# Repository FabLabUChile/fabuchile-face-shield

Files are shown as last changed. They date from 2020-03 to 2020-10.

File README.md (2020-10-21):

# Fablab U Chile Face Shield
Spanish version [here](/LEEME.md) | Versión en español [acá](/LEEME.md)

## Table of contents

- [Resume](#resume)
  * [Security and effectiveness validation](#security-and-effectiveness-validation)
- [Versions](#versions)
    + [LAST VERSION -> v6](#last-version----v6)
    + [v5 (can be stacked)](#v5--can-be-stacked-)
    + [v4](#v4)
    + [v3](#v3)
    + [v2](#v2)
    + [v1](#v1)
- [Parts](#parts)
  * [3D Printed Headband](#3d-printed-headband)
    + [Printer Settings](#printer-settings)
  * [Commercial Parts](#commercial-parts)
    + [Clear plastic sheet](#clear-plastic-sheet)
    + [Rubber band](#rubber-band)
- [Assembly](#assembly)
- [Sterilization and safety recommendations](#sterilization-and-safety-recommendations)
- [Join the community](#join-the-community)
- [License](#license)

<small><i><a href='http://ecotrust-canada.github.io/markdown-toc/'>Table of contents generated with markdown-toc</a></i></small>

## Resume

Based on the [Prusa Face Shield](https://www.prusaprinters.org/prints/25857-protective-face-shield-rc3) initiative, we design our own face shield in order to eliminate any further work on the comercial parts, and to match with the local availability of them,  decreasing the chance of contamination during the fabrication stage and for direct assembly. The face shield is meant to be used complementary with a N95 mask or similiar.

**Warning**: only V6.0 is a certificate medical device.

### Security and effectiveness validation

Recently, we subjected the V6.0 of the FaceShield to laboratory tests ([LICTEX USACH](https://www.linkedin.com/company/lictex-udesantiago/?originalSubdomain=cl)) to validate the performance of the Facial Shield (*)(**). The tests carried out were:
 1. Protection of standard point protected areas
 2. Protection against drops and liquid splashes
 3. Evaluation of lateral protection
 4. Evaluation of the Visual Field.

 (*) These tests are verified by the Chilean Institute of Public Health ([ISP](http://www.ispch.cl/)).
The Face Shield successfully passed all tests.

  (**) According to the standard of Facial Shields market in Chile, a fifth test is required, that of fogging. As we know, in Chile there are no laboratories that can carry out this test.

## Versions

#### LAST VERSION -> v6

The new version has several modifications in order to ensure protection over other factors:
* We increased the distances between the side flaps to use a legal size (~330 mm) translucent sheet. This modification gives more protection to the sides of the face.
* We added a cover in top of the shield to protect the face from particles that may attack from above.
* The cover increase the stiffness of the faceshield so we give more comfort by separating the side bars from the front part, also making it compliant for different head's sizes.

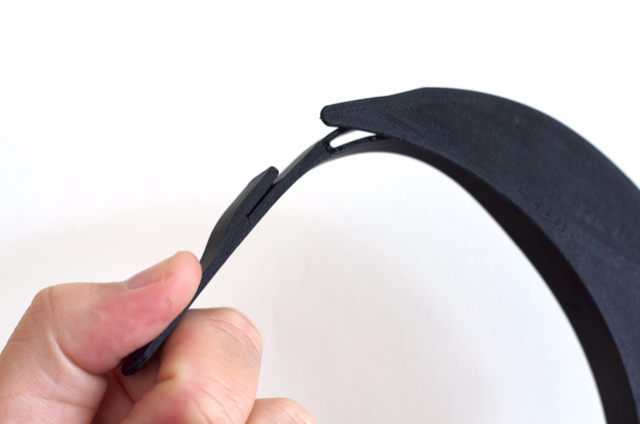
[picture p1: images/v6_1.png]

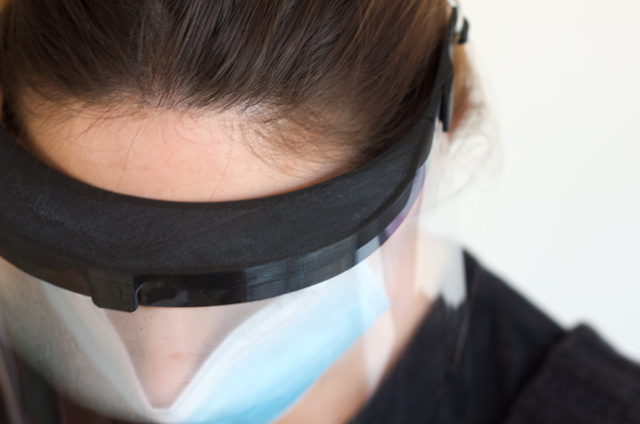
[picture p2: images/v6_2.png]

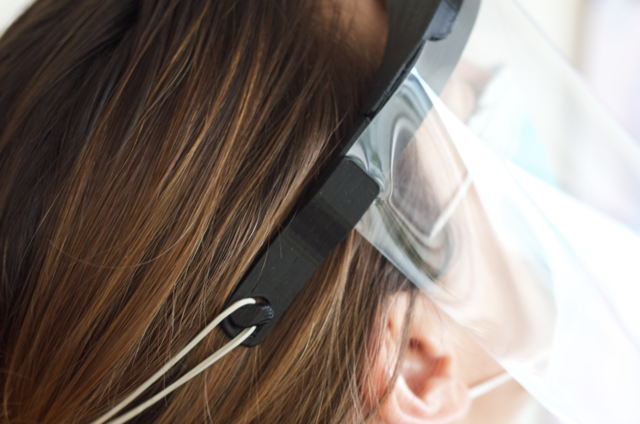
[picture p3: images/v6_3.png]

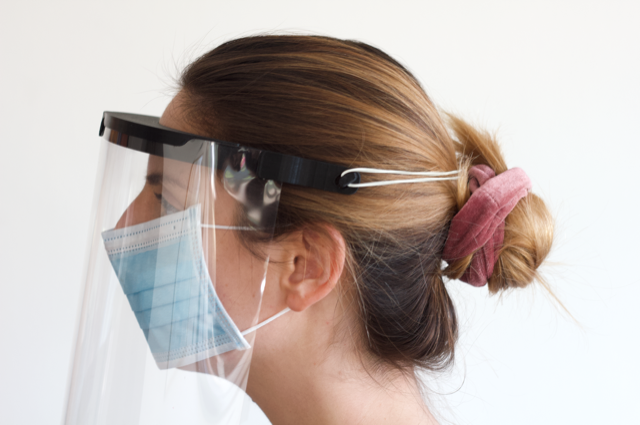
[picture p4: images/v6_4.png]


#### v5 (can be stacked)

The new version improves the comfortability in the usage, with wide open, almost paralel side bands, with a stronger structure to prevent breaking under strong undesirable forces. We also aded some minor improvements for stack printing.

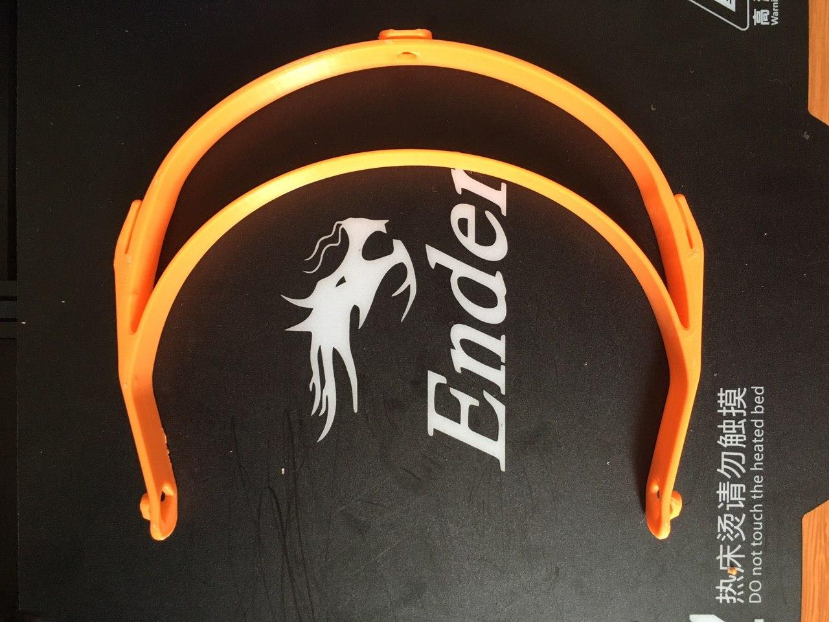
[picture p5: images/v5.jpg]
  

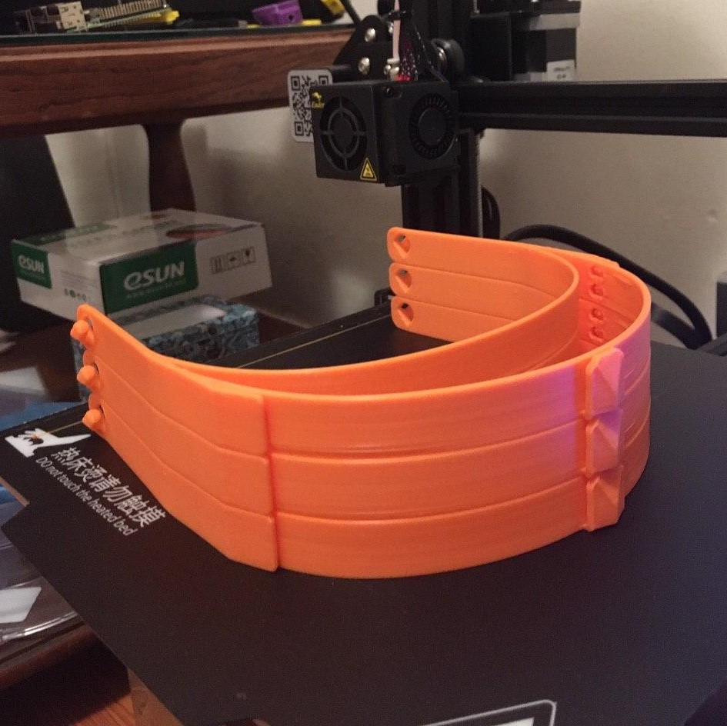
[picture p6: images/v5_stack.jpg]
v5_stack
  

#### v4

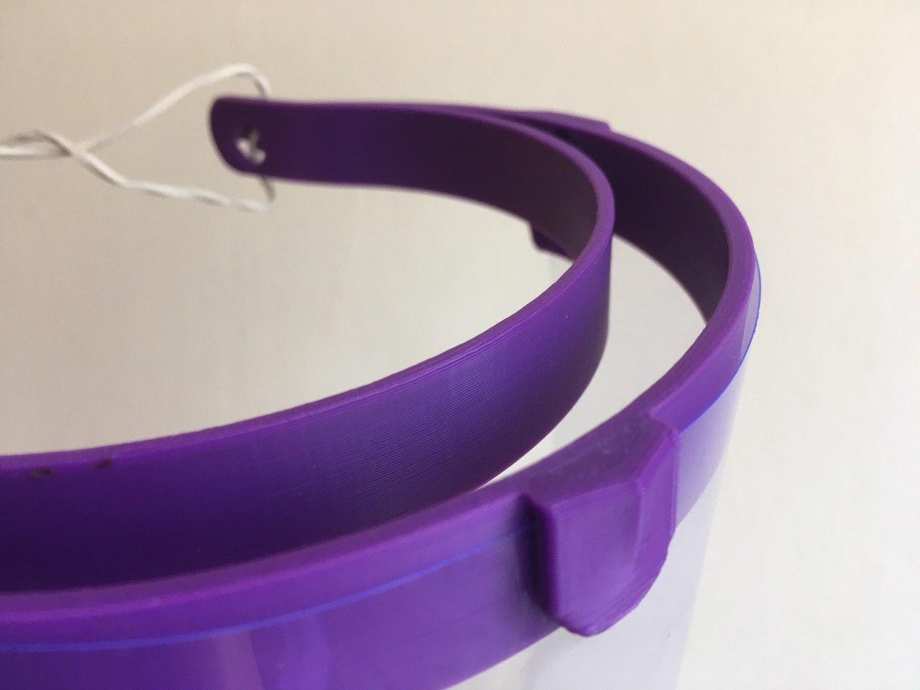
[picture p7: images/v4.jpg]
v4


#### v3

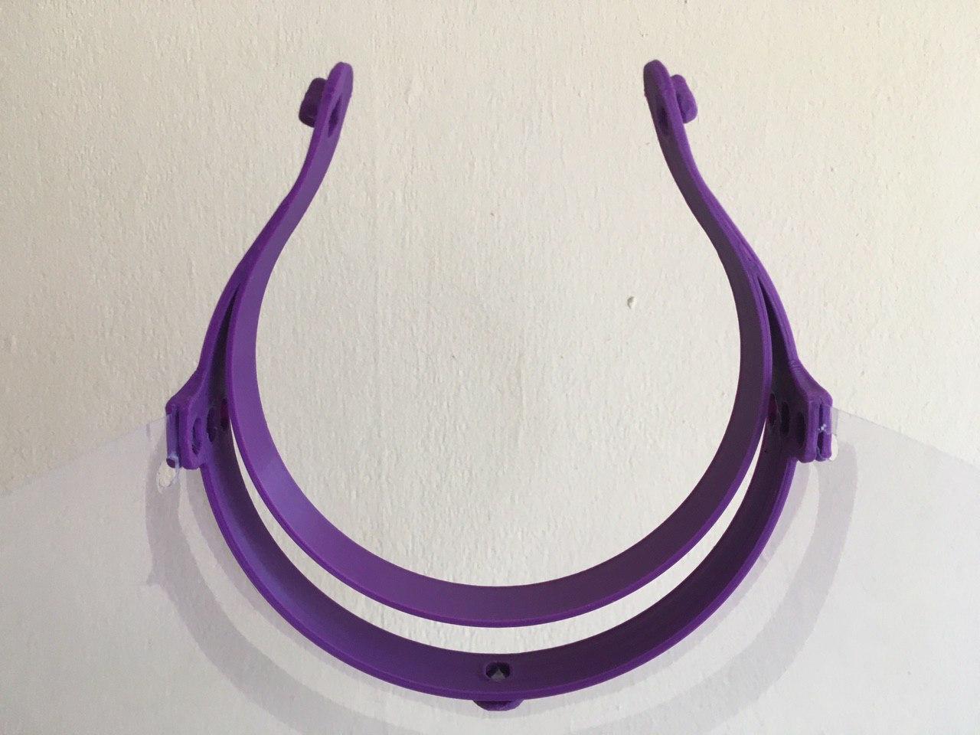
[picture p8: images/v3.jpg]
v3


#### v2

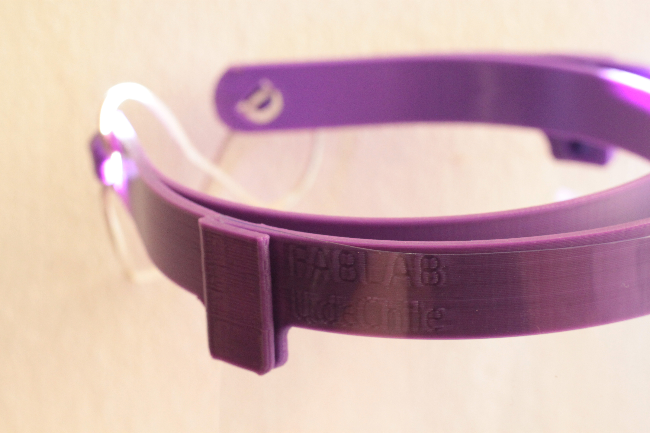
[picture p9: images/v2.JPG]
v2


#### v1

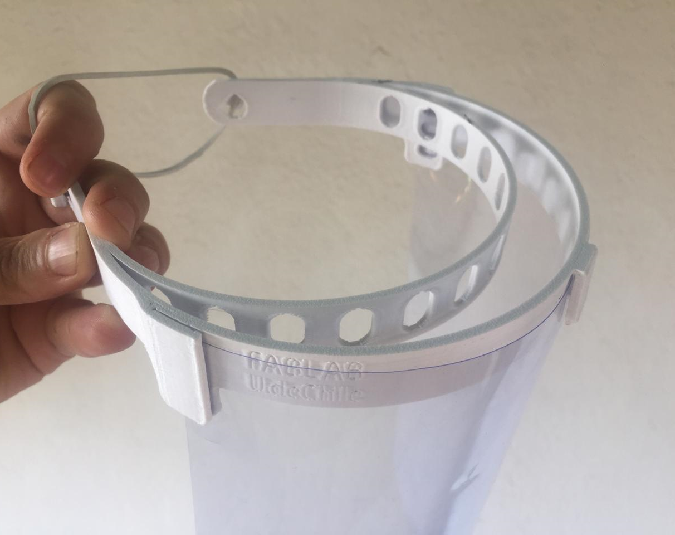
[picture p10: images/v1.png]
v1


## Parts

The device consists of three components:
* 3D printed headband
* Clear plastic sheet (*)
* Rubber band

```
* letter size (215.9 x 279mm) v1 to v5, portrait oriented, or
  legal size (215.9 x 330.2mm) v6, landscape oriented for side protection
```

### 3D Printed Headband

**YOU CAN GET THE FILES** at [PrusaPrinters](https://www.prusaprinters.org/prints/30347-fablab-u-de-chile-faceshield), [Thingiverse](https://www.thingiverse.com/thing:4250678)(STL) or [Grabcad](https://grabcad.com/library/covid-face-shield-2) (STL, STEP and F3D). Please check the version list, remember *this is a work in progress*.

Version | File Name                     | Release date
------- | ---------------------------   | ------------
V6.0    | face_shield_fabuchile_v6.stl	| 27-07
V5.0    | face_shield_fabuchile_v5.stl  | 22-04
V4.0    | faceshield_fablab_uch_v4.stl  | 06-04
V3.0	  | faceshield_fablab_uch_v3.stl	| 02-04
V2.0    | faceshield_fablab_uch_v2.stl  | 31-03
V1.0    | FaceShield_FabLab_UCH.stl     | 30-03

We recommend to print the headband in PLA, as is easier to print, no hot bed needed, compostable, has a low carbon footprint and it is tough enough. You can use a stronger filament if you want, like ABS or PETG, as long it is compatible with the sanitation measures that will be used on it.

The headband consist in two strips joint togheter in the ends. The inner strip goes around the head and the outer strip holds the clear sheet with some slip fits, far from the face to allow some room for glasses or goggles, also to avoid some fogging in the sheet due to breathing. The ends of the headband have a hook and holes to mount the rubber band, or another subjection device.

#### Printer Settings

V5 deployment on Cura, be sure the frontal slip fit and the rear hooks are upwards.
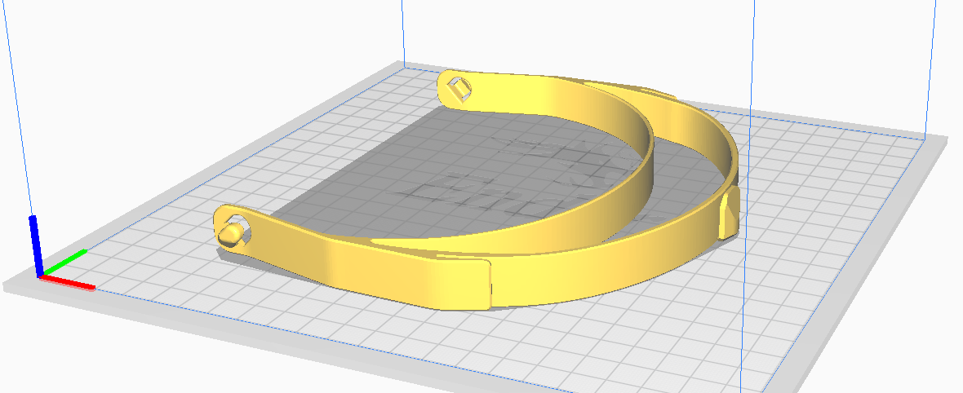
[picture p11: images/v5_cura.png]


We used some Ender 3 and Ender 5 3D printers to make the prototype and Cura as slicer, using the following parameters:

- Material: PLA
- Extruder Temp: 200°C
- Bed Temp: 60°C
- Layer Height: 0.3 mm
- Number of Shells: 3
- Infill density: 0% - 10% (many walls so this can be 0%)
- Speed: 60 mm/s infill, 30 mm/s walls.

You can also print two or more headbands stacked up, depending on the reliability of your printer. We have tested the stacked printings with 0.2mm separation in Z between each headband.

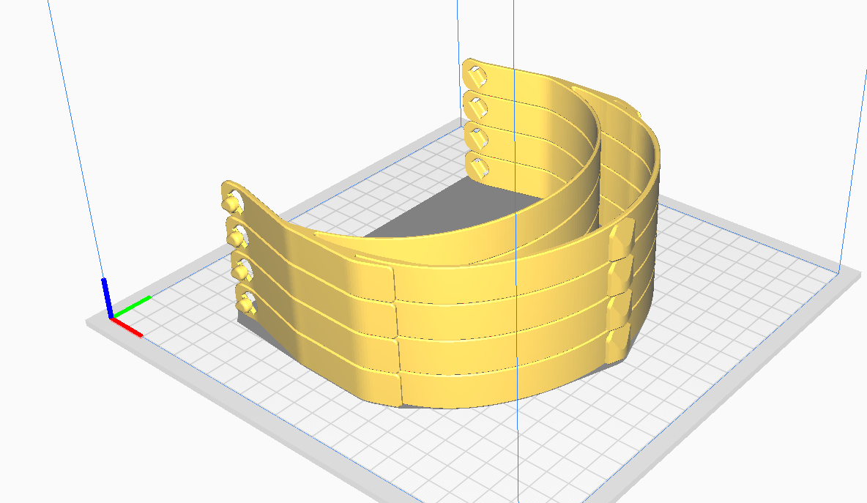
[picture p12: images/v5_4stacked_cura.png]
v5stacked


The only problem you may have with the printed part are the slip fits for supporting the clear sheet. It's optimized for 0.4 mm nozzle.
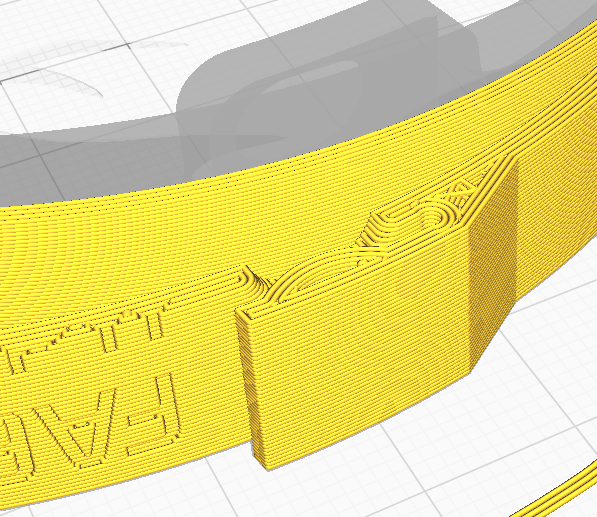
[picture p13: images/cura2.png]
difficult part step 1


### Commercial parts
the commercial parts needed for the full assembly of the face shield are
* a transparent plastic or mica sheet
* an elastic band

#### Transparent plastic sheet

The sheet is a cellulose acetate clear sheet, letter size (216X279 mm) or legal size (216x330 mm) vertical oriented for version 1 to 5) or legal size (216x330mm) horizontal oriented for v6, 0.2 mm thick. You can get some in almost any library or school supply store. It is possible to use a clear sheet of other material if it is available in the same size and if it is compatible with the available sanitation methods. You can also use the plastic of a 2-L bottle, if there is no other material available.

#### Elastic band

You can use any rubber band as long you feel comfortable with it, we used the most popular around here, [the money rubber band](https://www.aliexpress.com/i/32900926065.html).+

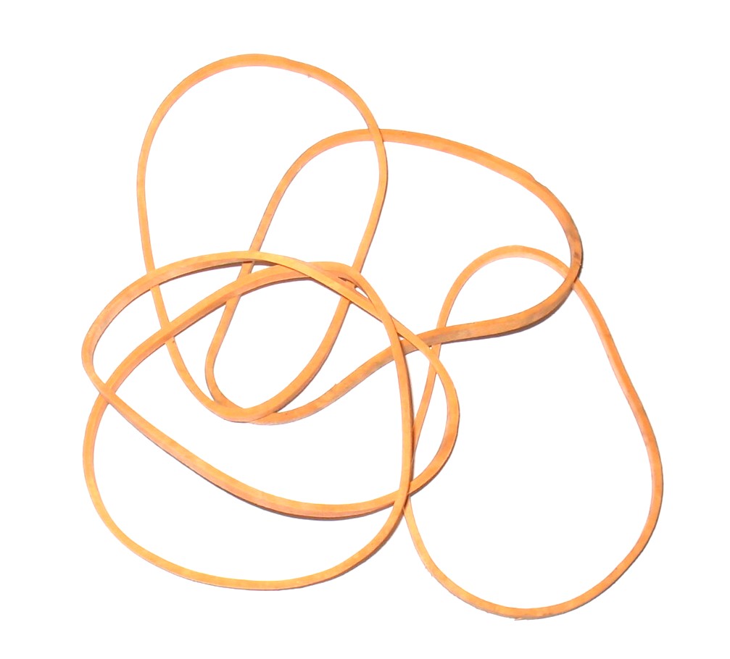
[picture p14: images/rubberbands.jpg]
rubber band step 1


## Assembly

After printing and sanitation of the parts, introduce the sheet in the fits of the headband in the outer strip as the picture below shows. Then, hook the rubber band in the headband ends. Ensure that the sheet is firm by pulling it gently. This is fundamental as otherwhise the user will be in danger of infection.

1. Put one corner of the sheet into one lateral fit

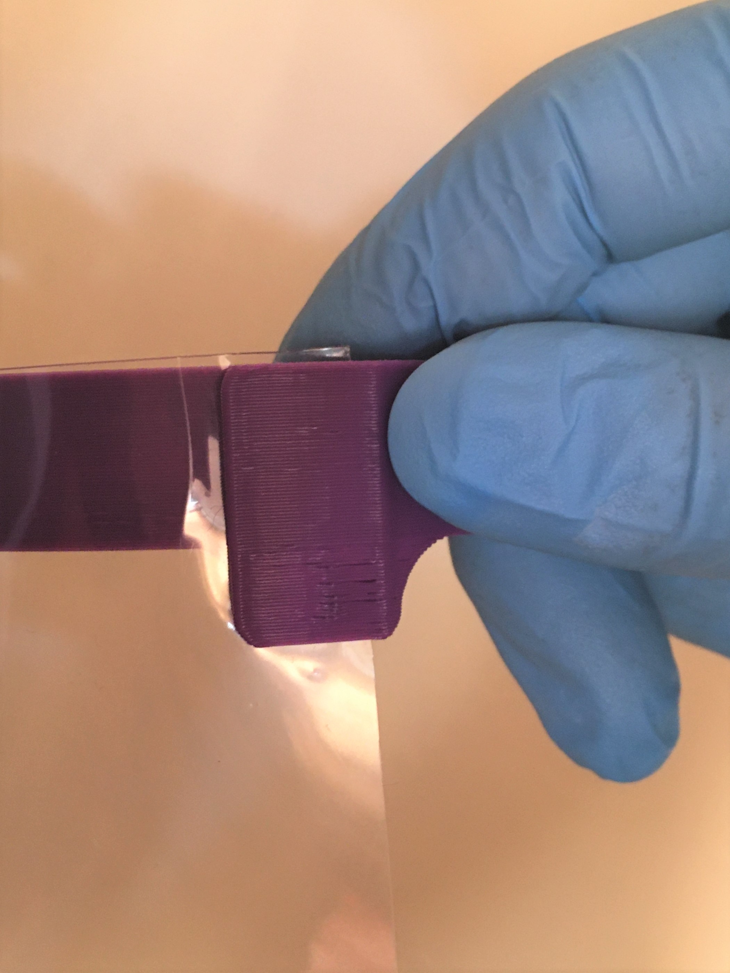
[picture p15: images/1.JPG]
step 1


2. Put the middle of the sheet in the frontal fit

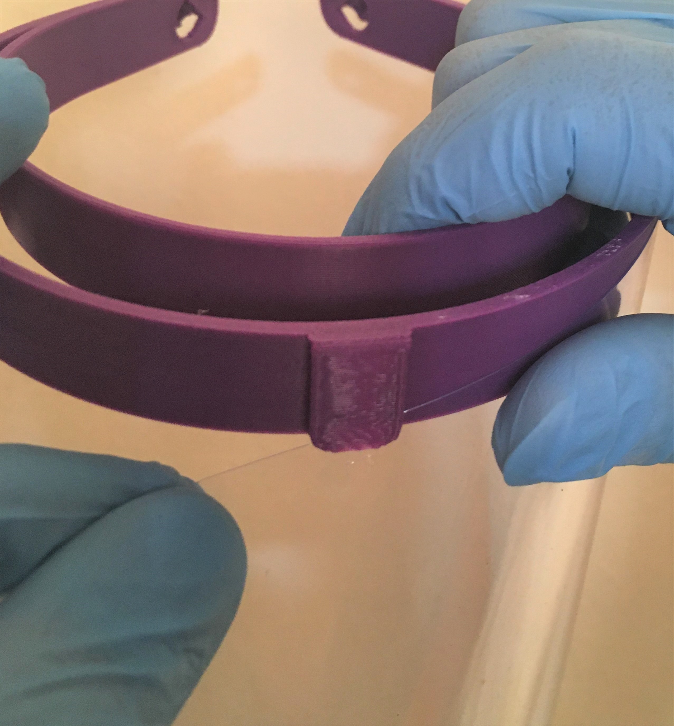
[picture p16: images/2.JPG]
step 2


3. Put the other corner of the sheet into the other lateral fit

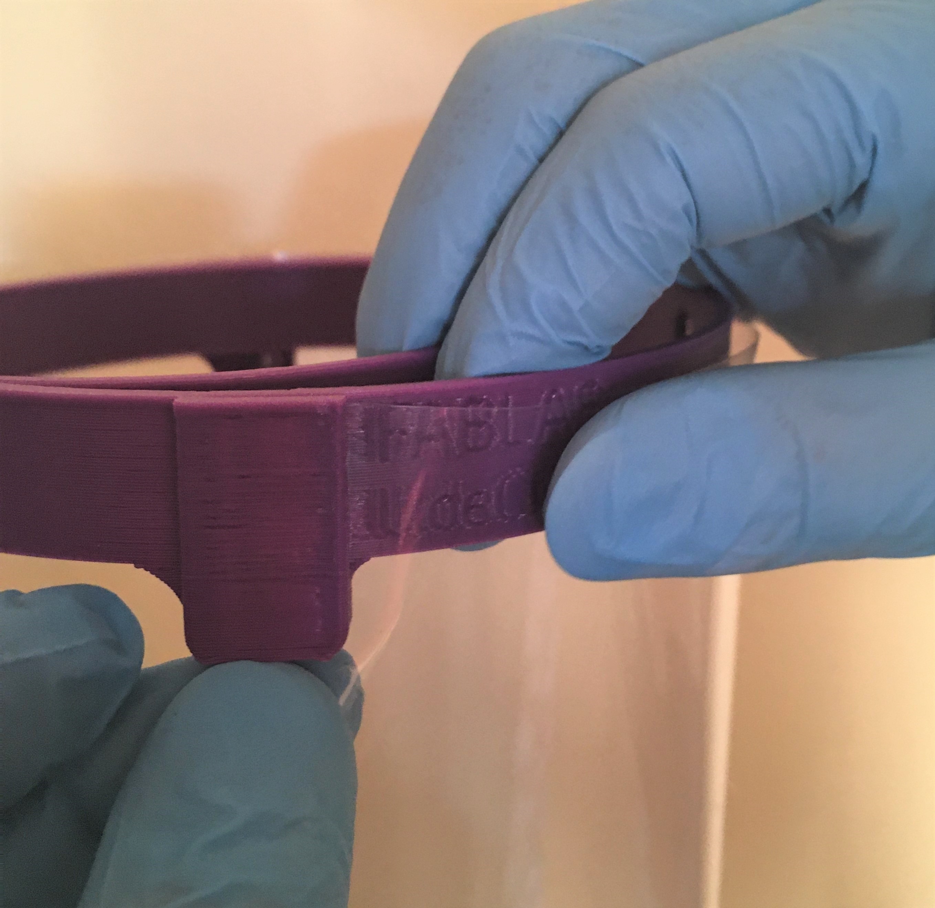
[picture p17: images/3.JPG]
step 3


4. Hook the ruber band in the headband ends

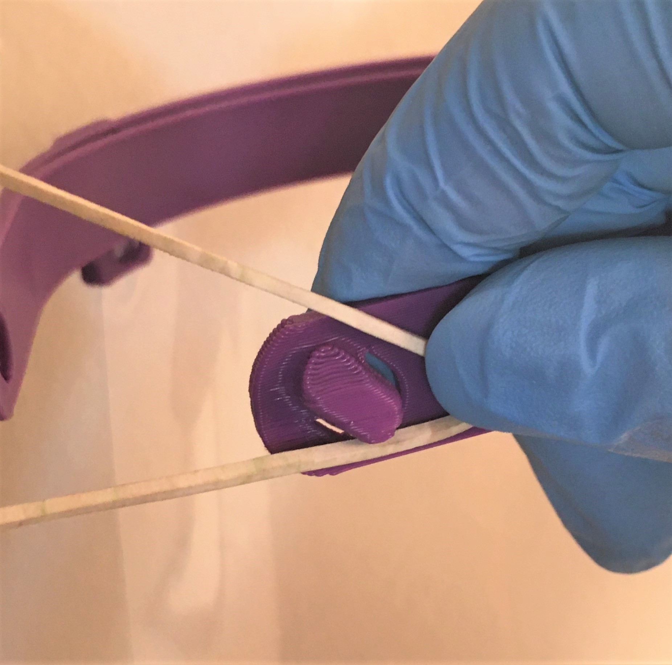
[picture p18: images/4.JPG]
step 4


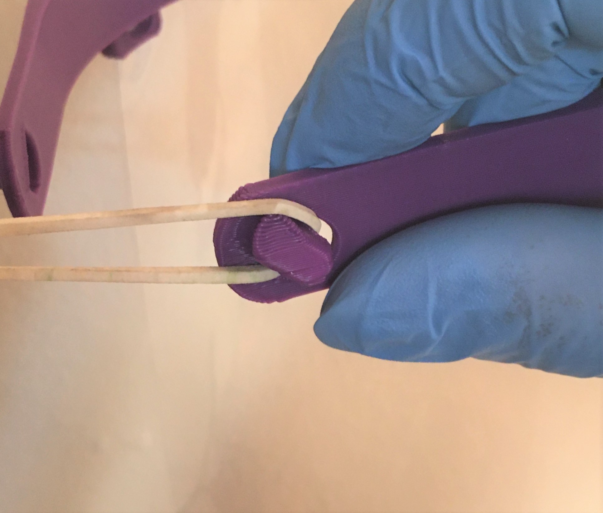
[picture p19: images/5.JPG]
step 5


## Sterilization and safety recommendations

During all the proccess, the components must be handled as if you were infected with Covid-19 virus, in a clean environment using clean gloves and mask to avoid cross contamination, and quickly stored in a plastic bag as soon it cools down after printing. [Recent studies](https://www.nejm.org/doi/full/10.1056/NEJMc2004973?query=featured_home) had revealed that the virus can last until 90 hours in plastic surfaces, so the headbands must be stored **three or four days** before delivery, unless the proper hygiene and sanitation protocols are being taken.

You can get updated information about sanitization of 3D printed faceshields in [this](https://help.prusa3d.com/en/article/prusa-face-shield-disinfection_125457#_ga=2.252887433.1803747422.1587586218-241505996.1587586218) article.

<!-- For sterilization at home, the [recommendations](https://www.minsal.cl/wp-content/uploads/2020/03/PROTOCOLO-DE-LIMPIEZA-Y-DESINFECCIÓN-DE-AMBIENTES-COVID-19.pdf) of ECDC are cleaning with 0,1% sodium hypoclorite (dilution 1:50 if household bleach at an initial concentration of 5% is used, 20mL in a 1L of water). *This is currently being verified by professionals*. -->

You can find more information about this proyect in [this brochure](/docs/LaminaFaceShield.pdf) or in the [AFES website](https://afeschile.cl).

<!-- You can take a look on [this list](https://www.epa.gov/pesticide-registration/list-n-disinfectants-use-against-sars-cov-2) for products that meet EPA’s criteria for use against SARS-CoV-2. -->

## Join the community

We encourage you to get involved and to make your part in this Covic-19 crisis. You can print the model, get the commercial parts, assemble the mask and share with those most in need.

If you think you can make an improvement of our face shield you can find the Fusion 360 cad, or STEP files [here][last-version]. Please **be serious** and test the functionality of your printed parts before you start producing and sharing them.

You can contact us in [facebook](https://www.facebook.com/fablabudechile/), [instagram](www.instagram.com/fablabudechile) or check our [webpage](www.fablab.uchile.cl).

[last-version]: https://github.com/FabLabUChile/fabuchile-face-shield/tree/master/cad/v6

## License

[][cc-by-sa]

This work is licensed under a [Creative Commons Attribution 4.0 International
License][cc-by-sa].

[][cc-by-sa]

[cc-by-sa]: https://creativecommons.org/licenses/by-sa/4.0/
[cc-by-sa-image]: https://i.creativecommons.org/l/by-sa/4.0/88x31.png
[cc-by-sa-shield]: https://img.shields.io/badge/License-CC%20BY%20SA%204.0-lightgrey.svg

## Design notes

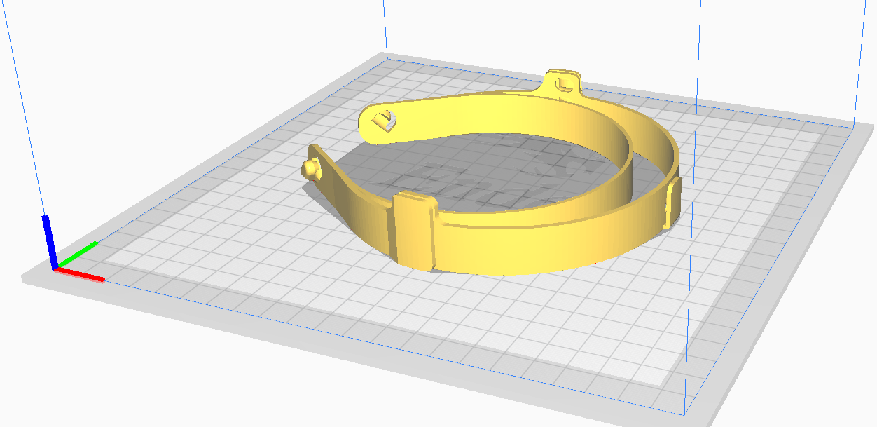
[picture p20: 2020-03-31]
images/cura1.png

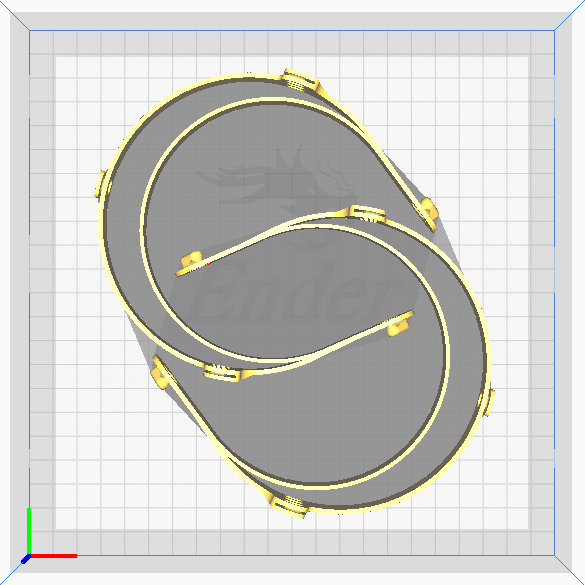
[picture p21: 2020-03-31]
images/curatwoheadbands.png

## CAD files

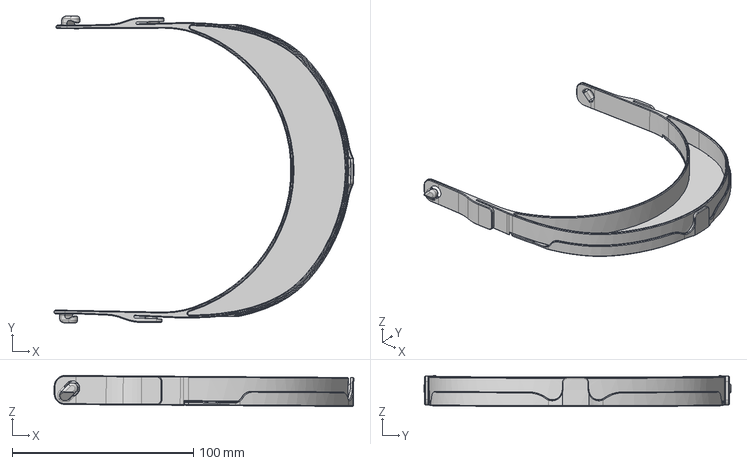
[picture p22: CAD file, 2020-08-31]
cad/v6/faceshield_fablab_uchile_v6.step
165.2 x 169.2 x 17.1 mm

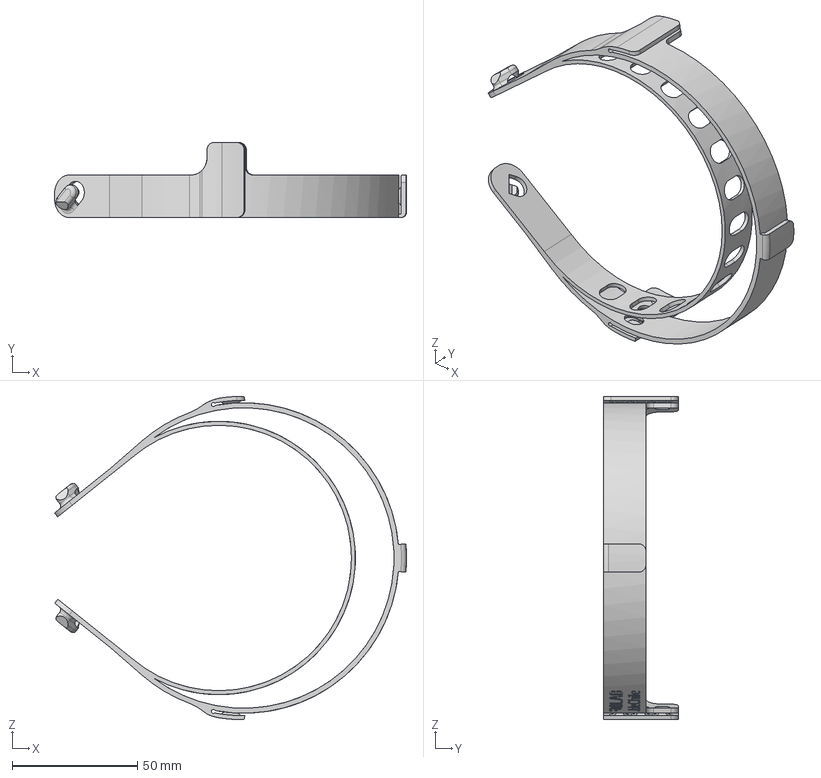
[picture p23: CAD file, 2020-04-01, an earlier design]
cad/v1/FaceShield_FabLab_UCH.step
140.6 x 30.0 x 129.2 mm

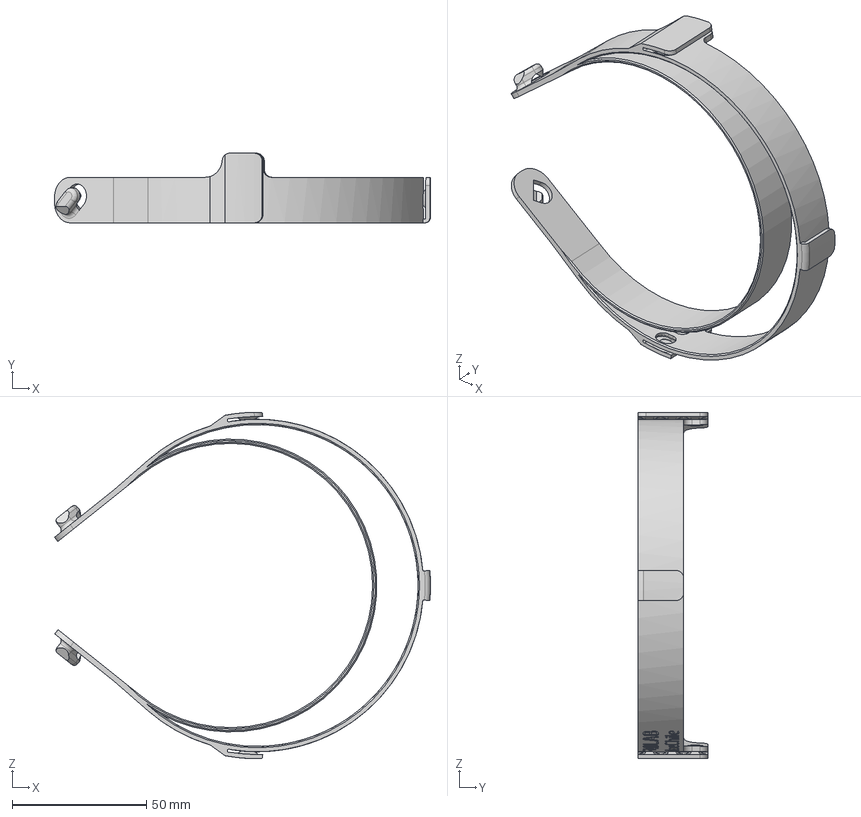
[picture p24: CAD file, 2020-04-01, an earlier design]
cad/v2/faceshield_fablab_uch_v2.step
140.2 x 26.0 x 129.2 mm

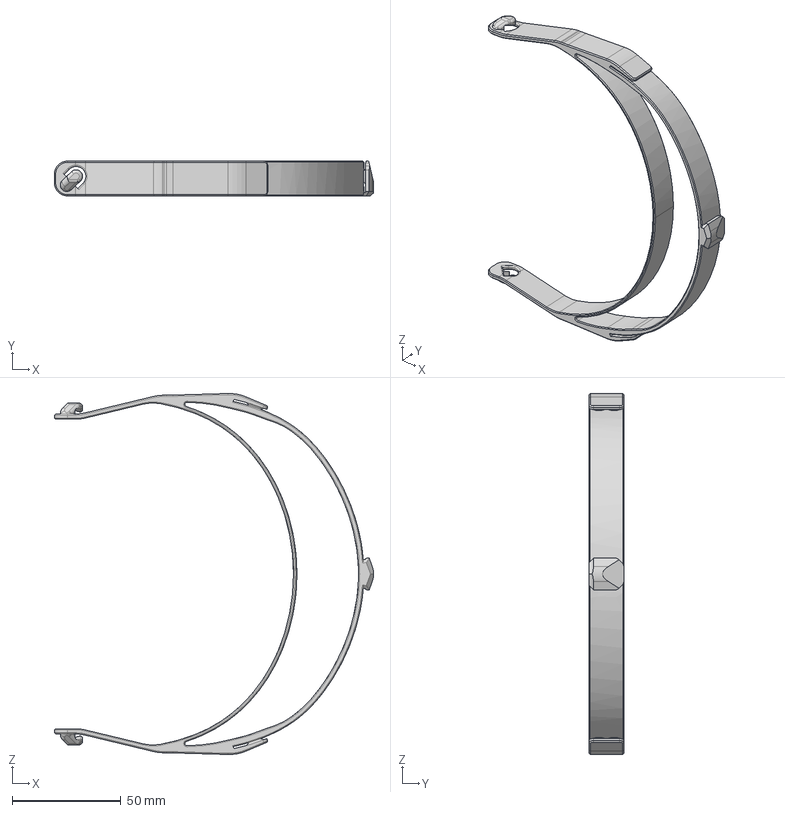
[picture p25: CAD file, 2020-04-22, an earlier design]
cad/v5/face_shield_fabuchile_v5.step
146.9 x 16.0 x 166.1 mm

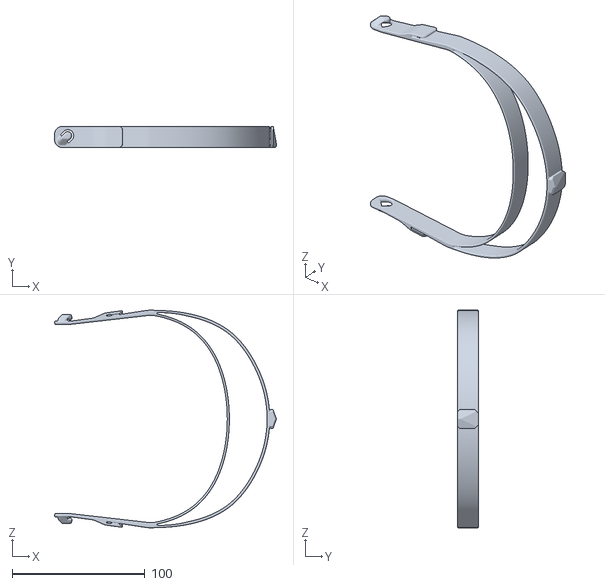
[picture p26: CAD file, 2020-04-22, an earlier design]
cad/v5/M3_340_v5.stl
167.1 x 16.0 x 163.7

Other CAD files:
cad/v3/face_shield_fabuchile_v3.step
cad/v4/face_shield_fabuchile_v4.step
cad/v1/FaceShield_FabLab_UCH.stl
cad/v2/faceshield_fablab_uch_v2.f3d
cad/v2/faceshield_fablab_uch_v2.stl
cad/v3/face_shield_fabuchile_v3.f3d
cad/v3/face_shield_fabuchile_v3.stl
cad/v4/face_shield_fabuchile_v4.f3d
cad/v4/face_shield_fabuchile_v4.stl
cad/v5/face_shield_fabuchile_v5.f3d
cad/v5/face_shield_fabuchile_v5.stl
cad/v6/faceshield_fablab_uchile_v6.stl

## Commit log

2020-03-25 Create FabUChile-face-shield.stl
    agregado stl versión 1
    [FabUChile-face-shield.stl]
2020-04-01 Update readme and add some files
    [FaceShield_FabLab_UCH.step, FaceShield_FabLab_UCH.stl, faceshield_fablab_uch_v2.f3d, faceshield_fablab_uch_v2.step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]
2020-04-02 added fashield v3
    [face_shield_fabuchile_v3.f3d, face_shield_fabuchile_v3.step, face_shield_fabuchile_v3.stl]
2020-04-06 updated version
    added v4 of the headband and more images to explain.
    [face_shield_fabuchile_v4.f3d, face_shield_fabuchile_v4.step, face_shield_fabuchile_v4.stl]
2020-04-22 added v5
    updated readme and added v5 headband
    [face_shield_fabuchile_v5.f3d, face_shield_fabuchile_v5.step, face_shield_fabuchile_v5.stl]
2020-04-22 updated readme v5
    [face_shield_fabuchile_v5.stl]
2020-04-22 upgraded readme
    [M3_340_v5.stl]
2020-07-29 v6 con vicera y mejoras menores para comodidad
    [faceshield_fablab_uchile_v6.step, faceshield_fablab_uchile_v6.stl]
2020-08-31 actualizado a v6
    [faceshield_fablab_uchile_v6.step, faceshield_fablab_uchile_v6.stl]
2020-09-28 updated v6 stl
    [faceshield_fablab_uchile_v6.stl]
2020-09-28 updated v6 stl file
    [faceshield_fablab_uchile_v6.stl]
2020-10-21 updated assembly instructions in readme
